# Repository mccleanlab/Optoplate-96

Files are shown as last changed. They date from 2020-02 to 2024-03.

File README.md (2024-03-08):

# OptoPlate-96
This repository contains the code  to calibrate and operate the [optoPlate-96](https://www.bugajlab.com/optoplate-96) and is intended to accompany the following paper:
E. O. S. Grødem, K. Sweeney, and M. N. McClean, “Automated calibration of optoPlate LEDs to reduce light dose variation in optogenetic experiments,” Biotechniques, vol. 69, no. 4, pp. 313–316, 2020.

To construct the optoPlate, see the original repository for the optoPlate-96 that can be found [here](https://github.com/BugajLab/optoPlate-96/) (as described in Bugaj and Lim, "High-throughput multicolor optogenetics in microwell plates" _Nature Protocols_ 14(7):2205-2228).

This repository was created to provide these features for the optoPlate-96:
- MATLAB interface for operation of the optoPlate-96.
- Functionality for calibration of the light intensities of the LEDs.
- Supports two levels of pulses to reduce the risk of phototoxicity.
- Visualisaztion of light patterns before an experiment.
- MultiColor LED support
- Support for turning on and off LED from a connected computer for microscope imagining

Machine learning scripts and data accompanying "Dynamic Multiplexed Control and Modeling of Optogenetic Systems Using the High-Throughput Optogenetic Platform, Lustro" (Harmer et al, BioRxiv 2023) can be found [here](https://github.com/zavalab/ML/tree/master/Optogenetics/)

Instructions and images for assembling the optoPlate with necessary adaptors can be found under "Mechanical".

## Installation:

- Install MATLAB
- Install Microsoft's Visual Studio Code and PlatformIO IDE by following these [instructions](https://platformio.org/install/ide?install=vscode)
- Install Platformio Shell Commands
  - In Windows Search, search for and then select: System (Control Panel)
  - Click the Advanced system settings link.
  - Click Environment Variables. In the section System Variables, find the PATH environment variable and select it. Click Edit. If the PATH environment variable does not exist, click New.
  - In the Edit enviroment variable window, create a new Path and paste `C:\Users\UserName\.platformio\penv\Scripts`. Make sure the new Path is on the top of the list. 
  - Click OK. Close all remaining windows by clicking OK.
You should now be able to flash the optoPlate-96 from your computer.

## Getting Started
If the optoPlate-96 has never been used before, it must be flashed with calibration values. Ideally the calibration procedure should be followed to calibrate the optoPlate to ensure consistent light intensities in the different wells. However, the optoPlate-96 will function with the default calibration values.
To flash the default calibration values, make sure the optoPlate is connected to the PC with an USB cable annd run the file calibration/FlashCalibration.m and select calibration/calibration_files/cal_round_0.mat. For instructions on how to calibrate the optoPlate see this article. 

To create an experiment, follow this procedure:
Create the following matrices:
- amplitudes [8 by 12 matrix of unsigned 8 bit integer] - light intensity of each LED, 255 - max light intensity and 0 - no light
- pulse_numbs [8 by 12 matrix of unsigned 16 bit integer] - number of pulses for each LED
- pusle_start_times [8 by 12 matrix of unsigned 16 bit integer] - time in seconds before sequence of pulses starts
- pulse_high_times [8 by 12 matrix of unsigned 16 bit integer] - time in seconds for high phase of pulse
- pulse_low_times [8 by 12 matrix of unsigned 16 bit integer] - time in seconds for low phase of pulse
- (optional) subpulse_high_times [8 by 12 matrix of unsigned 16 bit integer] - time in seconds for high phase of subpulse
- (optional) subpulse_low_times [8 by 12 matrix of unsigned 16 bit integer] - time in seconds for low phase of subpulse
Each cell in the matrices corresponds to a light well on the OptoPlate. For example, (1,1) is well A01 and (8,12) is well H12
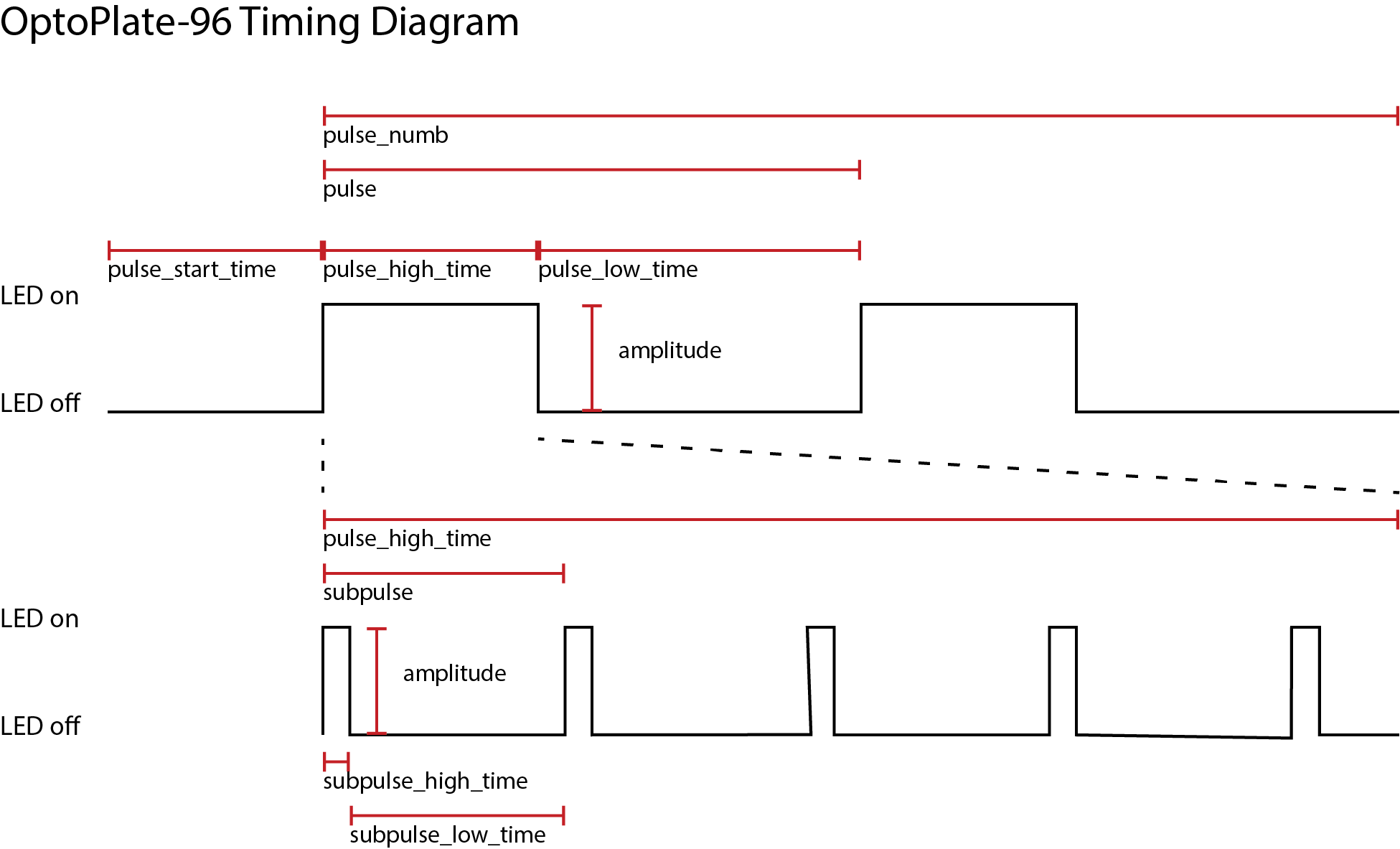
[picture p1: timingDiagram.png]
Timing Diagram

Create and save an experiment file by calling the function experiment/createExperiment.m
Make sure the OptoPlate is connected to the computer via an USB cable. Run the script experiment/FlashExperiment.m and select the experiment file.
The experiment will start immediately and will continue as long as the Arduino on the OptoPlate has power either through the USB cable or the 7V input. If power is cut to the Arduino, the experiment will reset. The experiment will also reset if the reset button on the Arduino is pressed.

## UART communication
Each well of the OptoPlate can be turned on and off by sending a UART message from the computer. This feature was added to support imagining with a microscope during an experiment. A detaljed description of how this works and a uart driver is provided in the folder OptoPlateDriver.

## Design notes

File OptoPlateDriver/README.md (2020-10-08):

# OptoPlate UART Driver 
This folder contains a driver written for use with the software NIS-elements AR. A custom driver can with ease be written for other purposes. '

## OptoPlate with NIS-elements AR
The diver can be imported into NIS micro. 
1. Visual Studio must be installed on the computer
2. To enable NIS to import the driver, copy the folder Optoplate-96/OptoPlateDiver/OptoPlate to the NIS installation folder most likely located in C:/Program Files/NIS-Elements. When this is done you should have the following file strucure: C:/Program Files/NIS-Elements/OptoPlate/OptoPlateDriver.dll
NIS Micros can now send commands to the OptoPlate. 

The following example of a micro will connect to Serial Port 14 and turn off all the LEDs in well 15 (B3). 
The OptoPlateConnectAuto() will search through the all connected serial ports and connect to one of them, this function can be used if the OptoPlate is the only serial port connected to the computer. In the case where there is more then one connected saerial port go to device manager in Windows to determine what port the optoPlate is connected to. It will be listed under "Ports (COM & LPT)" as "Arduino Micro Bootloader". Use the number after the COM in the function OptoPlateConnect(int) to connect to the optoPlate.  
Remember to always call OptoPlateConnect(int) or OptoPlateConnectAuto() before sending anything and always call OptoPlateDisconnect() before ending the program.
OptoPlateDiable(int) and OptoPlateEnable(int) takes an integer from 0 to 95 as input parameter. The index 15 correspond to the well B3 and index 16 to B4 and so on.  
```
import("OptoPlate\OptoPlateDriver.dll");
import int OptoPlateConnect(int portNumber);
import int OptoPlateConnectAuto();
import int OptoPlateDisconnect();
import int OptoPlateDisableLED(int LEDindex);
import int OptoPlateEnableLED(int LEDindex);

int main() {
   OptoPlateConnect(14);
   OptoPlateDisableLED(15);
   OptoPlateDisconnect();
   return 1;
}
                            
```
To change the index to be enable/diable while running a JOB module insert a Expression block. By opening the box you will get a list of all the variables used by the JOB module. The desired variable can then be used as parameter in the functions OptoPlateDiable(int) and OptoPlateEnable(int). A simple example is provided in Optoplate-96/OptoPlateDriver/NISexample    

## Help on implementation of custom driver
The OptoPlate accepts 1 byte messages over the Arduino Serial (UART) connection to the computer. The most significant bit is the enable/disable bit, the remaning 7 bits are the 0-indexed index of the well. For instance, by sending 0b0000 0010 over Serial, well A3 will turn off and 0b1000 1100 will enable enable well B1

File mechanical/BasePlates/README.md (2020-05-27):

The git repo for the original OptoPlate does not provide all the drawings for creating the aluminum plates in the assembly. 
These files can make the production of plates easier. 
They are taken from measurements and will therefore not be 100% precise.

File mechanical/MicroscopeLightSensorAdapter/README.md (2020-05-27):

Adaptor for mounting Thorlabs Standard Photodiode Power Sensors S12  to Nikon TiE inverted microscope

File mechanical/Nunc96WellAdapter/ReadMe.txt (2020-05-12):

Adapter for mounting a Nunc 265300 96 well plate to the OptoPlate. 
OptpPlateAdaperToNunc265300_Top is for mounting the 96 well plate upside down.

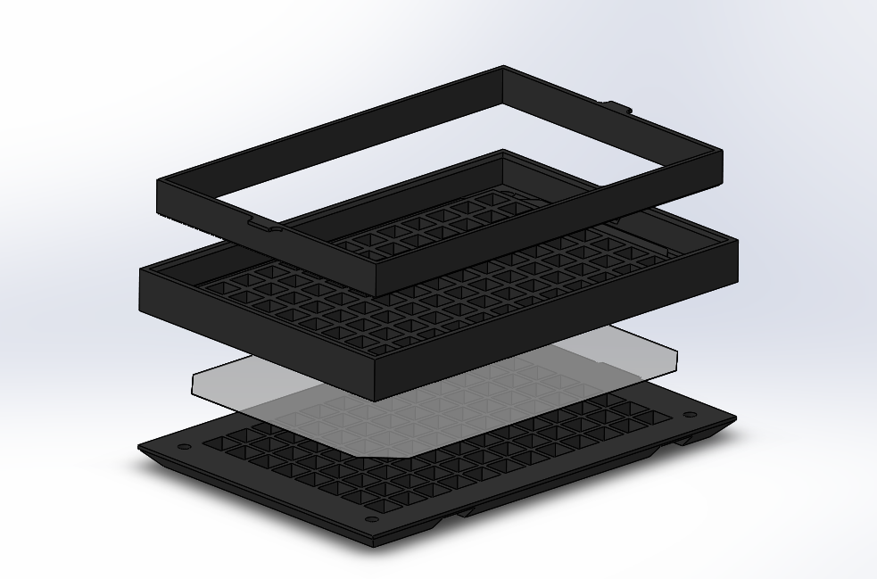
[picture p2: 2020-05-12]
mechanical/Nunc96WellAdapter/ExplodedViewRender.PNG

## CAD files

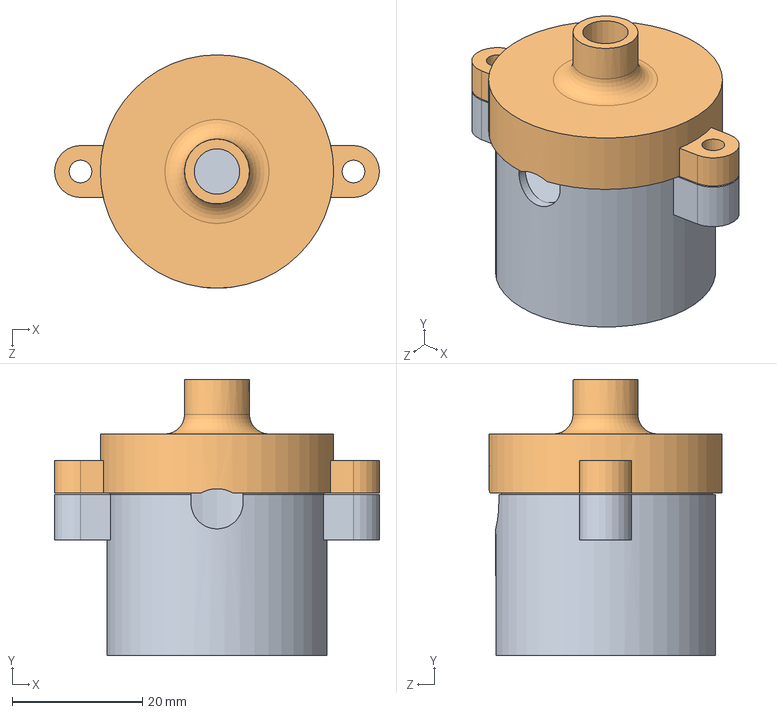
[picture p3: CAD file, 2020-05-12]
mechanical/MicroscopeLightSensorAdapter/AssemblyMicroscopeAdaptor.SLDASM
50.0 x 42.5 x 35.9 mm
MicroscopeAdapterLowerPart
MicroscopeAdapterUpperPart

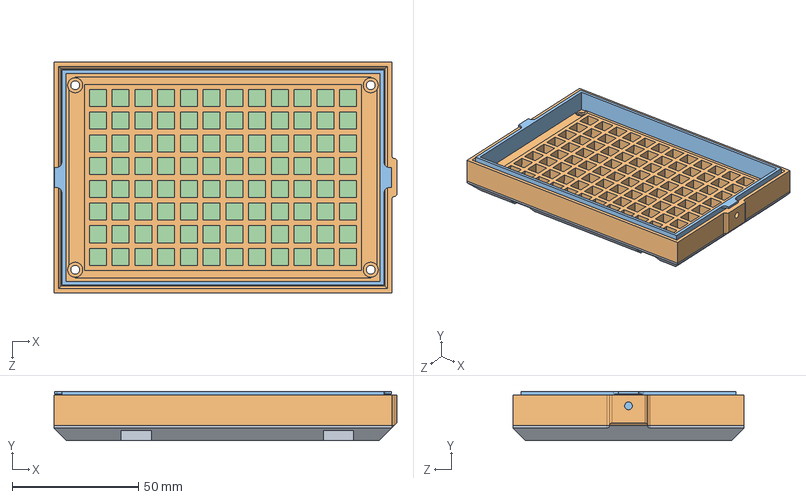
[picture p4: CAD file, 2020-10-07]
mechanical/Nunc96WellAdapter/OptoPlateAdapterToNunc265300_96_Assembly.SLDASM
135.8 x 19.5 x 91.5 mm
OptoPlateAdapterToNunc265300_96_BottomHalf
OptoPlateAdapterToNunc265300_96_Tophalf
Diffusion paper^OptoPlateAdapterToNunc265300_96_Assembly

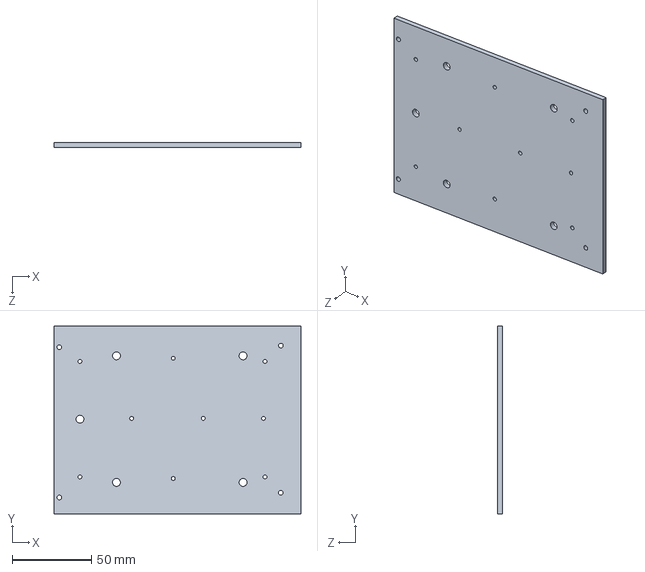
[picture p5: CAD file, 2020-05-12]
mechanical/BasePlates/Aluminum Plate.SLDPRT
156.1 x 118.5 x 3.17 mm

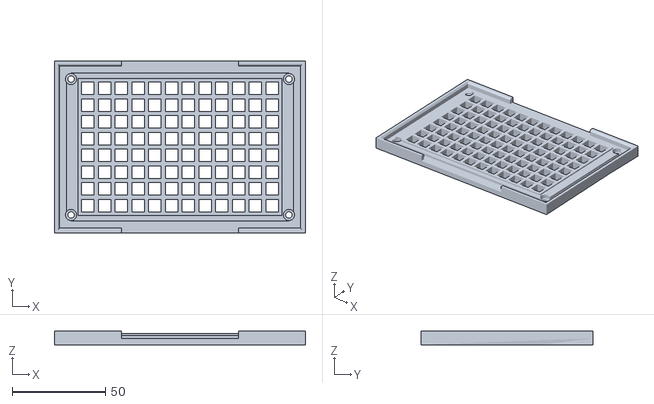
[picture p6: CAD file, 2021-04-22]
mechanical/Nunc96WellAdapter/3dprint/OptoPlateAdapterToNunc265300_96_Tophalf_TECAN.STL
134.8 x 92.5 x 7.29

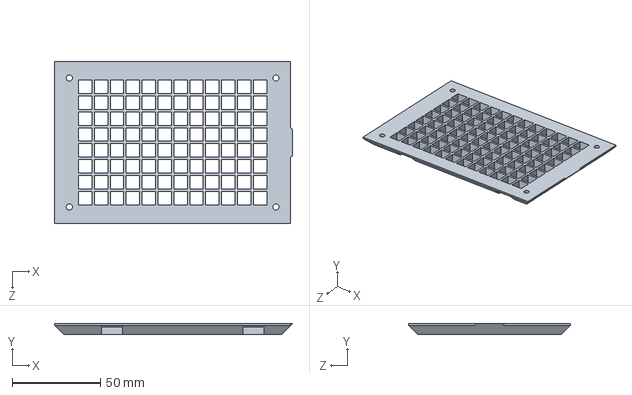
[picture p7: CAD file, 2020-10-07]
mechanical/Nunc96WellAdapter/OptoPlateAdapterToNunc265300_96_BottomHalf.sldprt
134.8 x 6.00 x 91.5 mm

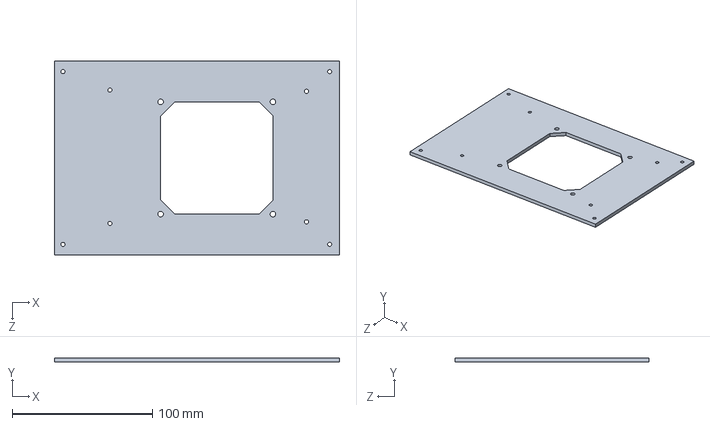
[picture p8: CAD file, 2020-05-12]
mechanical/BasePlates/Base Plate.SLDPRT
203.0 x 3.17 x 138.0 mm

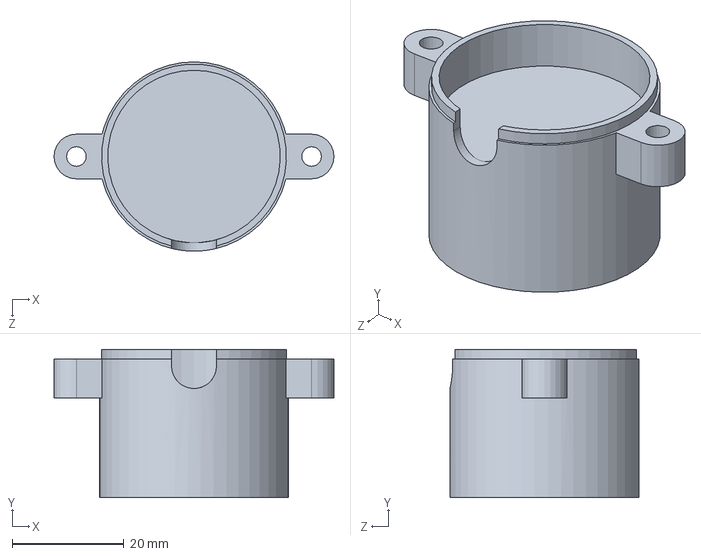
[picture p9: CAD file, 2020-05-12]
mechanical/MicroscopeLightSensorAdapter/MicroscopeAdaptorLowerPart.SLDPRT
50.0 x 26.5 x 33.8 mm

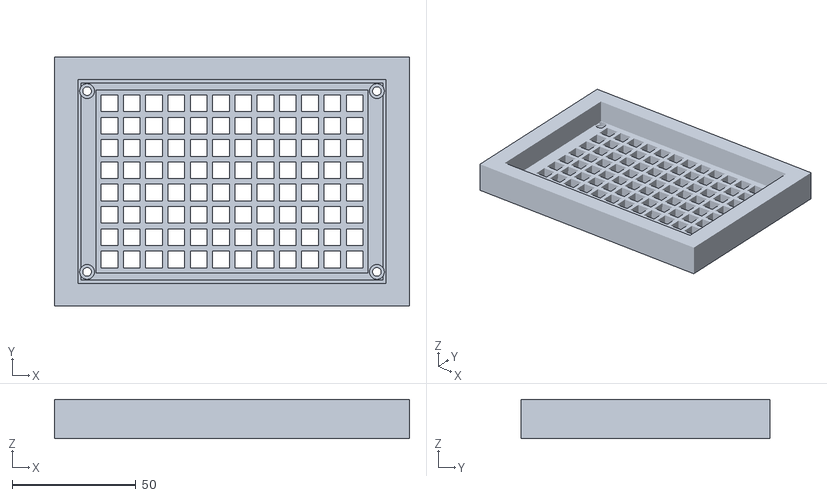
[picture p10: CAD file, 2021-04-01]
mechanical/Nunc96WellAdapter/3dprint/OptoPlateAdapterToNunc265300_96_Tophalf_Inverted.STL
143.3 x 100.5 x 15.9

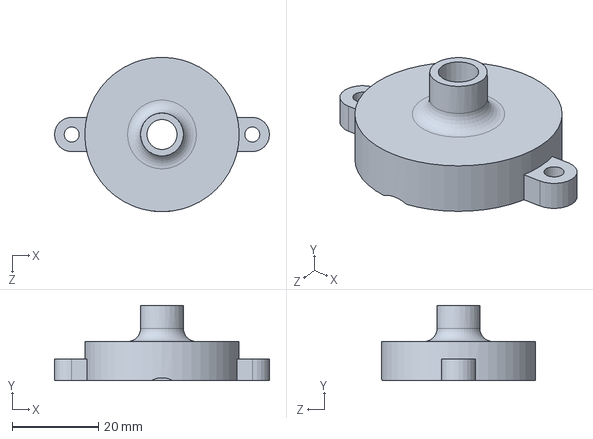
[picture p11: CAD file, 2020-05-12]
mechanical/MicroscopeLightSensorAdapter/MicroscopeAdaptorUpperPart.SLDPRT
50.0 x 17.5 x 35.9 mm

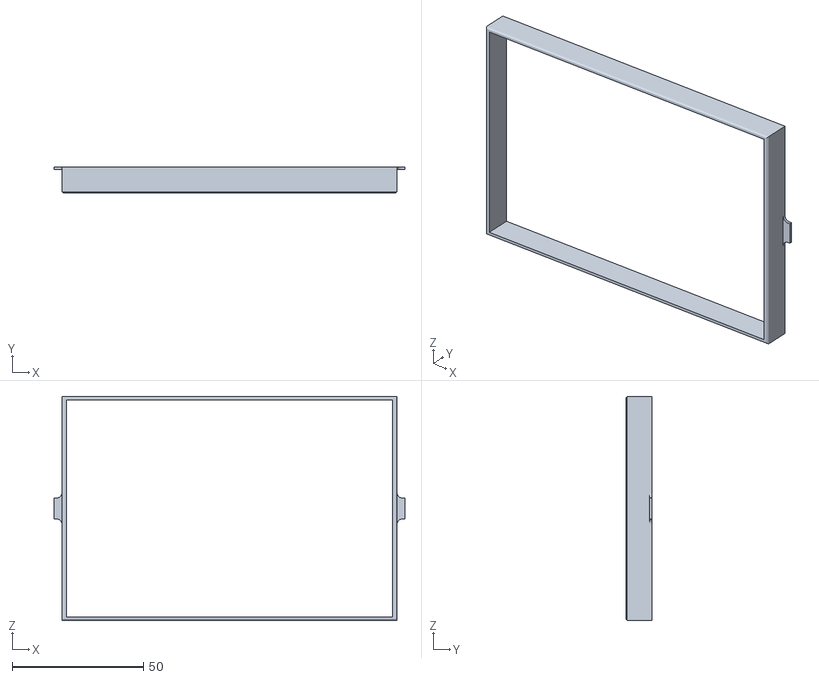
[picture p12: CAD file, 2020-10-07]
mechanical/Nunc96WellAdapter/3dprint/OptoPlateAdapterToNunc265300_96_InversionInsert_Default.STL
133.6 x 10.0 x 85.3

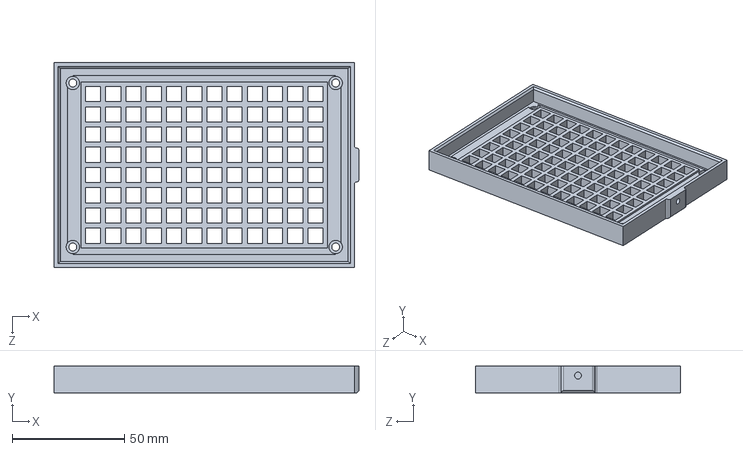
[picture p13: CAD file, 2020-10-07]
mechanical/Nunc96WellAdapter/OptoPlateAdapterToNunc265300_96_Tophalf.sldprt
135.8 x 12.0 x 91.5 mm

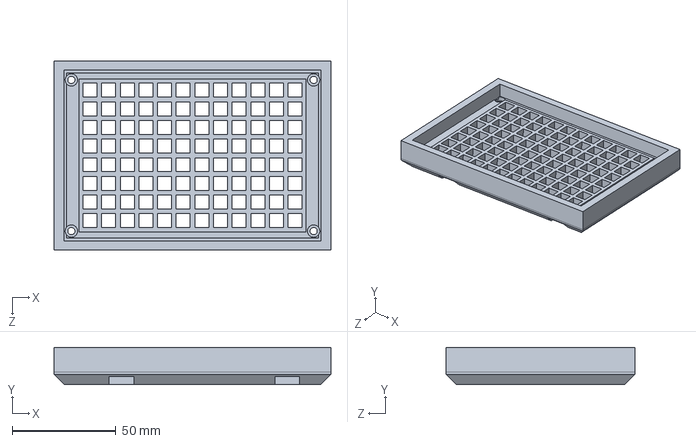
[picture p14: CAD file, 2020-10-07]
mechanical/Nunc96WellAdapter/OptoPlateAdapterToNunc265300_96.SLDPRT
133.8 x 18.0 x 91.5 mm

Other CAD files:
mechanical/Nunc96WellAdapter/3dprint/OptoPlateAdapterToNunc265300_96_BottomHalf_Default.STL
mechanical/Nunc96WellAdapter/3dprint/OptoPlateAdapterToNunc265300_96_Tophalf_Default.STL
mechanical/Nunc96WellAdapter/OptoPlateAdapterToNunc265300_96_InversionInsert.SLDPRT
mechanical/BasePlates/Aluminum Plate.SLDDRW
mechanical/BasePlates/Base Plate.SLDDRW

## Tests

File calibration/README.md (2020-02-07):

# optoPlate_calibration
 MATLAB script to calibrate optoPlate from images

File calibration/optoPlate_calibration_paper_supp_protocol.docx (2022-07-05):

Supplementary protocol

Configuring the optoPlate

We assemble the optoPlate as published [1], but with two changes to suit the needs of our lab and allow calibration. First, we adapt the optoPlate to accommodate 96 well optical-bottom plates (Nunc, #265300) via 3D printed adaptors. By default, these adaptors allow one to mount the 96 well plate on top of the optoPlate, though we also created a secondary adaptor to mount the optoPlate upside-down on top of the 96 well plate. The optoPlate can be equipped with these adaptors by following these steps (Figure S1):

1. Mount the optoPlateToNunc265300_BottomHalf adaptor to the optoPlate PCB
2. Place three diffuser sheets (Rosco, #3008) on top of the optoPlateToNunc265300_BottomHalf adaptor
3. Mount the optoPlateToNunc265300_TopHalf adaptor on top of the diffuser sheets. At this stage, a Nunc 96 well optical-bottom plate can be mounted on top of the optoPlate
4. Slot the optoPlateToNunc265300_Top adaptor into the optoPlateToNunc265300_TopHalf. The optoPlate can now be mounted upside-down on top of a Nunc 96 well optical-bottom plate.

Second, we developed new firmware for the optoPlate so the brightness of each LED is controlled by both a calibration value and an input value as follows:

LED intensity∝(input values)/255*(calibration values)/255

The input value is supplied by a user to control LED brightness over the course of an experiment. The calibration value must be set only once and accounts for brightness differences between LEDs, so that two LEDs set to the same input value will have the same brightness. The optoPlate firmware was built using PlatformIO and the onboard Arduino and it allows users to design LED light programs and flash them to the optoPlate using MATLAB.

The firmware and hardware used in this protocol are supplied in our supplementary materials. Updates will be made available on our GitHub page (github.com/mccleanlab/ OptoPlate-96). Installation of the firmware is described in detail in the included README file, as are instructions for creating light programs for experiments and flashing them to the optoPlate.

Calibrating the optoPlate with two LEDs

Our calibration method uses the programmable stage of a microscope to automatically move an optical power sensor over each optoPlate LED in a set order to acquire a timeseries of irradiance measurements from which the brightness of each LED can be determined and used to calculate calibration values. To ensure that each LED creates a distinct peak in the irradiance signal, we do not measure all the LEDs in one pass. Instead we measure all LEDs over the course of four passes in which we raster the optical power meter across the optoPlate such that every other LED encountered is inactive, leading to an irradiance signal in which measurements from inactive LEDs create clear troughs between measurements of bright LEDs. We do this by setting the optoPlate to deliver a checkerboard illumination pattern, such that no two illuminated wells are directly above, below, or beside each other in a given pass. We measure the remaining wells by setting the optoPlate to deliver the inverse checkerboard illumination pattern. Because each well of the optoPlate has two LEDs, we repeat this process twice, once for the left LED and once for the right LED. Once all 192 LEDs are measured, we analyze the irradiance measurements using a MATLAB script that determines the brightness of each LED and calculates a calibration value so that the brightest LEDs are dimmest to match the dimmest LED. We then flash the calibration values to the optoPlate and repeat the whole process until the coefficient of variation of the LED irradiance measurements falls below a set threshold (we use 1%).

In detail, this can be accomplished by following these steps (Figure S2):

1. First, mount a refocusing unit [2] to the active objective socket of a Nikon TiE inverted microscope. Then (as shown in Figure S3A) fasten the optical power sensor (Thorlabs S120VC) between the upper and lower optical power sensor adaptors (MicroscopeAdaptorLowerPart and MicroscopeAdaptorUpperPart, respectively) and mount the resulting assembly on the refocusing unit. Then connect the Thorlabs power sensor to a Thorlabs power meter (PM100D), which should be connected to a computer running Thorlabs Optical Power Monitor Version 1.1 software.
2. Mount a Nunc 96 well optical-bottom plate to the microscope stage (Figure S3B). Then mount the optoPlate upside-down on top of the 96 well plate via the optoPlateToNunc265300_Top adaptor. The optoPlate should be positioned so that well A1 of the optoPlate is positioned over well A12 of the 96 well plate. Plug in the optoPlate and connect it to a computer via the USB cable. To finish preparing the microscope for calibration, adjust its focus knob to raise the optical power sensor until it nearly touches the 96 well plate. Note the z-position of the stage and use it for all future measurements (we always use a z-position of 4000 μm). This approach allows consistent micron level precision when setting the distance between the optical power sensor and optoPlate.
3. Flash the initial set of calibration values to the optoPlate by running the MATLAB script ‘flash_calibration.m’ and selecting the file ‘cal_round_0’ at the prompt. This sets the initial calibration value of each LED to 255.
4. Making sure that the optical power meter is set to measure the appropriate wavelength for each set of LEDs, measure the brightness of the LEDs by using the programmable microscope stage to raster the optical power sensor across the 96 well plate:
  a. Flash the first checkerboard illumination pattern to the optoPlate by running ‘FlashExperiment.m’ and selecting ‘CHECKER01.mat’ when prompted. Then unplug the power cable for the right LEDs so that only the left LEDs of every other well are active. Start recording irradiance measurements with the power meter software, then have the microscope stage raster through the 96 well plate, pausing at each well for 3 s (Figure 1A). We did this via a NIS Elements JOBs module program. Save these measurements as ‘ROUND01_LED01_CHECKER01.csv’; they should resemble the signals depicted in Figure 1B.
  b. Unplug the power cable for the left LEDs and plug in the power cable for the right LEDs, then record LED irradiance measurements as described in step 4a. Save these measurements as ‘ROUND01_LED02_CHECKER01.csv’.
  c. Flash the second checkerboard illumination pattern to the optoPlate by running ‘flash_experiment.m’ and selecting ‘CHECKER02.mat’ when prompted. Record the LED irradiance measurements for both sets of LEDs as described above and save them as ‘ROUND01_LED01_CHECKER02.csv’ and ‘ROUND01_LED02_CHECKER02.csv’.
5. With all LEDs now measured, run the MATLAB script ‘optoPlate_calibration.m’ and select the saved ‘.csv’ files at the prompt. Note that this script uses the GRAMM toolbox for plotting, which can be found, along with installation instructions, at github.com/piermorel/gramm. The script will automatically identify each LED from the irradiance measurements and calculate calibration values, which are saved as ‘cal_round_1.mat’. It should be noted that this script assumes the wells are measured in a set order in which 1) the microscope rasters through a 96 well plate mounted on its programmable stage from A1-A12 to B12-B1 and so on and 2) the optoPlate is flipped when mounted upside-down on the 96 well plate so that these measurements actually correspond to optoPlate wells A12-A1 to B1-B12 etc. Flashing the optoPlate with CHECKER01.mat sets the checkerboard pattern in which the LEDs of optoPlate well A01 are active, while CHECKER02.mat sets the checkerboard pattern in which the LEDs of optoPlate well A01 are inactive. By default, the calibration script assumes an optoPlate configuration with two LEDs of the same color per well. If this is not the case, set the variable ‘calibrate_LEDs_independently’ to true and the script will treat each set of LEDs (LED01, LED02, etc.) as separate groups of different colored LEDs when calculating calibration values.
6. Flash the updated calibration values to the optoPlate. This concludes round one of calibration. The brightness of the LEDs should be much more uniform, though more rounds of calibration may be needed to further reduce brightness differences between LEDs.
7. Repeat steps 4 – 6 as needed until the coefficient of variation of the LED irradiance measurements falls below a set threshold (we chose 1%). Each of these repeats constitutes another round of calibration. When saving the ‘csv’ files, the round number should be included in the filename, for example, the left LED measurements for the first checkerboard illumination pattern of round two should be saved as ‘ROUND02_LED01_CHECKER01.csv’. Likewise, when loading the measurements into ‘optoPlate_calibration.m’ or flashing calibration values to the optoPlate, be sure to use the measurements or calibration values for the current round.

Calibrating an optoPlate with three LEDs

In the preceding protocol, we described the calibration of an optoPlate with two LEDs per well. However, an optoPlate can also be configured to have three different colored LEDs per well. In this case, the overall calibration process is similar, but involves six measurement passes—one per LED color for each checkerboard pattern. With three LEDs per well, one must switch between active LED sets by flashing checkerboard patterns for each color rather than reconnecting the power cables. As before, one must set ‘calibrate_LEDs_independently’ to true and set the optical power meter to measure the correct light wavelength for each set of LEDs.

Supplementary figure captions

Figure S1. Assembly of the optoPlate-to-Nunc265300 adaptors

Figure S2. A flow chart detailing the optoPlate calibration process

Figure S3. Overview of the components used for calibration. (A) An optical power meter is prepared for mounting on the microscope. (B) The optical power meter and optoPlate are mounted to a microscope.

1. Bugaj LJ, Lim WA. High-throughput multicolor optogenetics in microwell plates. Nat. Protoc. 14(7), 2205–2228 (2019).

2. Grünwald D, Shenoy SM, Burke S, Singer RH. Calibrating excitation light fluxes for quantitative light microscopy in cell biology. Nat. Protoc. 3(11), 1809–1814 (2008).

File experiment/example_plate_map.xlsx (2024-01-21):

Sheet: optoplate_config
LED1_amplitudes | 1 | 2 | 3 | 4 | 5 | 6 | 7 | 8 | 9 | 10 | 11 | 12 | LED2_amplitudes | 1 | 2 | 3 | 4 | 5 | 6 | 7 | 8 | 9 | 10 | 11 | 12 | LED3_amplitudes | 1 | 2 | 3 | 4 | 5 | 6 | 7 | 8 | 9 | 10 | 11 | 12
A | 0 | 128 | 0 | 128 | 0 | 0 | 0 | 0 | 0 | 0 | 0 | 0 | A |  |  |  |  |  |  |  |  |  |  |  |  | A
B | 20 | 128 | 20 | 128 | 0 | 0 | 0 | 0 | 0 | 0 | 0 | 0 | B |  |  |  |  |  |  |  |  |  |  |  |  | B
C | 45 | 128 | 45 | 128 | 0 | 0 | 0 | 0 | 0 | 0 | 0 | 0 | C |  |  |  |  |  |  |  |  |  |  |  |  | C
D | 85 | 128 | 85 | 128 | 0 | 0 | 0 | 0 | 0 | 0 | 0 | 0 | D |  |  |  |  |  |  |  |  |  |  |  |  | D
E | 128 | 128 | 128 | 128 | 0 | 0 | 0 | 0 | 0 | 0 | 0 | 0 | E |  |  |  |  |  |  |  |  |  |  |  |  | E
F | 128 | 128 | 128 | 128 | 0 | 0 | 0 | 0 | 0 | 0 | 0 | 0 | F |  |  |  |  |  |  |  |  |  |  |  |  | F
G | 128 | 128 | 128 | 128 | 0 | 0 | 0 | 0 | 0 | 0 | 0 | 0 | G |  |  |  |  |  |  |  |  |  |  |  |  | G
H | 128 | 128 | 128 | 0 | 0 | 0 | 0 | 0 | 0 | 0 | 0 | 0 | H |  |  |  |  |  |  |  |  |  |  |  |  | H
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

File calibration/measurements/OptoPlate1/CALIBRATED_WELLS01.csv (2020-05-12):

Optical Power Monitor
2.1.3076.429
Delimiter Used: | " | "
Start of Measurement | 3/11/2020 13:45:51
Sample Interval | 1 s
 | PM100D 15111301
Type | PM100D
Serialnumber | PM001960
Sensor | S120VC
SensorSerialnumber | 15111301
Wavelength / Responsivity | 488 nm
 |  |  | PM100D 15111301
Samples | Date (MM/dd/yyyy) | Time of day (hh:mm:ss) | Irradiance (W/cm²)
0 | 3/11/2020 | 13:45:51 | 1.4892E-07
1 | 3/11/2020 | 13:45:52 | 2.1814E-07
2 | 3/11/2020 | 13:45:53 | 2.0168E-07
3 | 3/11/2020 | 13:45:54 | 1.8654E-07
4 | 3/11/2020 | 13:45:55 | 2.392E-07
5 | 3/11/2020 | 13:45:56 | 1.8805E-07
6 | 3/11/2020 | 13:45:57 | 1.8052E-07
7 | 3/11/2020 | 13:45:58 | 1.5193E-07
8 | 3/11/2020 | 13:45:59 | 2.0911E-07
9 | 3/11/2020 | 13:46:00 | 1.8805E-07
10 | 3/11/2020 | 13:46:01 | 1.9707E-07
11 | 3/11/2020 | 13:46:02 | 5.8075E-07
12 | 3/11/2020 | 13:46:03 | 0.00017204
13 | 3/11/2020 | 13:46:04 | 0.00018895
14 | 3/11/2020 | 13:46:05 | 0.00018844
15 | 3/11/2020 | 13:46:06 | 9.2623E-05
16 | 3/11/2020 | 13:46:07 | 3.3248E-07
17 | 3/11/2020 | 13:46:08 | 3.1443E-07
18 | 3/11/2020 | 13:46:09 | 1.4444E-06
19 | 3/11/2020 | 13:46:10 | 0.00017526
20 | 3/11/2020 | 13:46:11 | 0.00018944
21 | 3/11/2020 | 13:46:12 | 0.00018967
22 | 3/11/2020 | 13:46:13 | 8.5935E-05
23 | 3/11/2020 | 13:46:14 | 3.6258E-07
24 | 3/11/2020 | 13:46:15 | 3.2948E-07
25 | 3/11/2020 | 13:46:16 | 3.3613E-06
26 | 3/11/2020 | 13:46:17 | 0.00018259
27 | 3/11/2020 | 13:46:18 | 0.00019082
28 | 3/11/2020 | 13:46:19 | 0.00018978
29 | 3/11/2020 | 13:46:20 | 0.00019081
30 | 3/11/2020 | 13:46:21 | 3.559E-05
31 | 3/11/2020 | 13:46:22 | 3.3851E-07
32 | 3/11/2020 | 13:46:23 | 3.0992E-07
33 | 3/11/2020 | 13:46:24 | 4.7949E-05
34 | 3/11/2020 | 13:46:25 | 0.00018731
35 | 3/11/2020 | 13:46:26 | 0.00018731
36 | 3/11/2020 | 13:46:27 | 0.00018752
37 | 3/11/2020 | 13:46:28 | 2.7843E-05
38 | 3/11/2020 | 13:46:29 | 3.385E-07
39 | 3/11/2020 | 13:46:30 | 2.9638E-07
40 | 3/11/2020 | 13:46:31 | 5.3616E-05
41 | 3/11/2020 | 13:46:32 | 0.00018876
42 | 3/11/2020 | 13:46:33 | 0.00018805
43 | 3/11/2020 | 13:46:34 | 0.00018868
44 | 3/11/2020 | 13:46:35 | 2.3159E-05
45 | 3/11/2020 | 13:46:36 | 3.2797E-07
46 | 3/11/2020 | 13:46:37 | 3.4452E-07
47 | 3/11/2020 | 13:46:38 | 5.9923E-05
48 | 3/11/2020 | 13:46:39 | 0.00019009
49 | 3/11/2020 | 13:46:40 | 0.00019072
50 | 3/11/2020 | 13:46:41 | 0.00018964
51 | 3/11/2020 | 13:46:42 | 2.5072E-05
52 | 3/11/2020 | 13:46:43 | 2.8885E-07
53 | 3/11/2020 | 13:46:44 | 3.0089E-07
54 | 3/11/2020 | 13:46:45 | 5.3238E-05
55 | 3/11/2020 | 13:46:46 | 0.00018887
56 | 3/11/2020 | 13:46:47 | 0.00018843
57 | 3/11/2020 | 13:46:48 | 0.0001883
58 | 3/11/2020 | 13:46:49 | 2.3934E-05
59 | 3/11/2020 | 13:46:50 | 4.3029E-07
60 | 3/11/2020 | 13:46:51 | 4.2126E-07
61 | 3/11/2020 | 13:46:52 | 5.6047E-05
62 | 3/11/2020 | 13:46:53 | 0.00018837
63 | 3/11/2020 | 13:46:54 | 0.0001875
64 | 3/11/2020 | 13:46:55 | 0.00018726
65 | 3/11/2020 | 13:46:56 | 2.0118E-05
66 | 3/11/2020 | 13:46:57 | 4.9047E-07
67 | 3/11/2020 | 13:46:58 | 4.7994E-07
68 | 3/11/2020 | 13:46:59 | 5.966E-05
69 | 3/11/2020 | 13:47:00 | 0.00019029
70 | 3/11/2020 | 13:47:01 | 0.00019017
71 | 3/11/2020 | 13:47:02 | 0.00018925
72 | 3/11/2020 | 13:47:03 | 1.7208E-05
73 | 3/11/2020 | 13:47:04 | 4.4382E-07
74 | 3/11/2020 | 13:47:05 | 4.1524E-07
75 | 3/11/2020 | 13:47:06 | 6.2761E-05
76 | 3/11/2020 | 13:47:07 | 0.00018796
77 | 3/11/2020 | 13:47:08 | 0.00018821
78 | 3/11/2020 | 13:47:09 | 0.00018833
79 | 3/11/2020 | 13:47:10 | 1.7293E-05
80 | 3/11/2020 | 13:47:11 | 4.5135E-07
81 | 3/11/2020 | 13:47:12 | 4.5586E-07
82 | 3/11/2020 | 13:47:13 | 6.5287E-05
83 | 3/11/2020 | 13:47:14 | 0.00018891
84 | 3/11/2020 | 13:47:15 | 0.0001879
85 | 3/11/2020 | 13:47:16 | 0.00018749
86 | 3/11/2020 | 13:47:17 | 1.3704E-05
87 | 3/11/2020 | 13:47:18 | 4.0471E-07
88 | 3/11/2020 | 13:47:19 | 3.9417E-07
89 | 3/11/2020 | 13:47:20 | 6.7406E-05
90 | 3/11/2020 | 13:47:21 | 0.00018756
91 | 3/11/2020 | 13:47:22 | 0.00018933
92 | 3/11/2020 | 13:47:23 | 0.0001866
93 | 3/11/2020 | 13:47:24 | 1.2404E-05
94 | 3/11/2020 | 13:47:25 | 3.365E-07
95 | 3/11/2020 | 13:47:26 | 3.6709E-07
96 | 3/11/2020 | 13:47:27 | 3.5204E-07
97 | 3/11/2020 | 13:47:28 | 0.00012836
98 | 3/11/2020 | 13:47:29 | 0.00018951
99 | 3/11/2020 | 13:47:30 | 0.00018942
100 | 3/11/2020 | 13:47:31 | 0.00013738
101 | 3/11/2020 | 13:47:32 | 4.7091E-07
102 | 3/11/2020 | 13:47:33 | 4.5436E-07
103 | 3/11/2020 | 13:47:34 | 4.1524E-07
104 | 3/11/2020 | 13:47:35 | 0.00012958
105 | 3/11/2020 | 13:47:36 | 0.0001887
106 | 3/11/2020 | 13:47:37 | 0.00018876
107 | 3/11/2020 | 13:47:38 | 0.00013406
108 | 3/11/2020 | 13:47:39 | 5.2357E-07
109 | 3/11/2020 | 13:47:40 | 4.1674E-07
110 | 3/11/2020 | 13:47:41 | 4.679E-07
111 | 3/11/2020 | 13:47:42 | 0.00013328
112 | 3/11/2020 | 13:47:43 | 0.00018759
113 | 3/11/2020 | 13:47:44 | 0.00018736
114 | 3/11/2020 | 13:47:45 | 0.00013211
115 | 3/11/2020 | 13:47:46 | 5.1605E-07
116 | 3/11/2020 | 13:47:47 | 4.4081E-07
117 | 3/11/2020 | 13:47:48 | 4.6941E-07
118 | 3/11/2020 | 13:47:49 | 0.00013591
119 | 3/11/2020 | 13:47:50 | 0.00018752
120 | 3/11/2020 | 13:47:51 | 0.00018766
121 | 3/11/2020 | 13:47:52 | 0.00012946
122 | 3/11/2020 | 13:47:53 | 4.5135E-07
123 | 3/11/2020 | 13:47:54 | 5.0401E-07
124 | 3/11/2020 | 13:47:55 | 4.5587E-07
125 | 3/11/2020 | 13:47:56 | 0.00013936
126 | 3/11/2020 | 13:47:57 | 0.00018807
127 | 3/11/2020 | 13:47:58 | 0.00018802
128 | 3/11/2020 | 13:47:59 | 0.00012273
129 | 3/11/2020 | 13:48:00 | 4.4533E-07
130 | 3/11/2020 | 13:48:01 | 4.047E-07
131 | 3/11/2020 | 13:48:02 | 4.6038E-07
132 | 3/11/2020 | 13:48:03 | 0.00014478
133 | 3/11/2020 | 13:48:04 | 0.00018847
134 | 3/11/2020 | 13:48:05 | 0.00018779
135 | 3/11/2020 | 13:48:06 | 0.00012703
136 | 3/11/2020 | 13:48:07 | 3.2045E-07
137 | 3/11/2020 | 13:48:08 | 2.9186E-07
138 | 3/11/2020 | 13:48:09 | 2.7381E-07
139 | 3/11/2020 | 13:48:10 | 0.00013569
140 | 3/11/2020 | 13:48:11 | 0.00018765
141 | 3/11/2020 | 13:48:12 | 0.00018697
142 | 3/11/2020 | 13:48:13 | 0.00012682
143 | 3/11/2020 | 13:48:14 | 4.5135E-07
144 | 3/11/2020 | 13:48:15 | 4.7091E-07
145 | 3/11/2020 | 13:48:16 | 4.3781E-07
146 | 3/11/2020 | 13:48:17 | 0.00014017
147 | 3/11/2020 | 13:48:18 | 0.00018579
148 | 3/11/2020 | 13:48:19 | 0.0001864
149 | 3/11/2020 | 13:48:20 | 0.0001247
150 | 3/11/2020 | 13:48:21 | 4.9799E-07
151 | 3/11/2020 | 13:48:22 | 4.4984E-07
152 | 3/11/2020 | 13:48:23 | 4.5285E-07
153 | 3/11/2020 | 13:48:24 | 0.00013965
154 | 3/11/2020 | 13:48:25 | 0.00018666
155 | 3/11/2020 | 13:48:26 | 0.00018718
156 | 3/11/2020 | 13:48:27 | 0.00012303
157 | 3/11/2020 | 13:48:28 | 4.8897E-07
158 | 3/11/2020 | 13:48:29 | 4.363E-07
159 | 3/11/2020 | 13:48:30 | 4.4984E-07
160 | 3/11/2020 | 13:48:31 | 0.0001445
161 | 3/11/2020 | 13:48:32 | 0.00018847
162 | 3/11/2020 | 13:48:33 | 0.00018728
163 | 3/11/2020 | 13:48:34 | 0.00018719
164 | 3/11/2020 | 13:48:35 | 6.9849E-05
165 | 3/11/2020 | 13:48:36 | 4.6188E-07
166 | 3/11/2020 | 13:48:37 | 4.3329E-07
167 | 3/11/2020 | 13:48:38 | 1.1388E-05
168 | 3/11/2020 | 13:48:39 | 0.00018791
169 | 3/11/2020 | 13:48:40 | 0.00018764
170 | 3/11/2020 | 13:48:41 | 0.00018962
171 | 3/11/2020 | 13:48:42 | 6.9074E-05
172 | 3/11/2020 | 13:48:43 | 4.6941E-07
173 | 3/11/2020 | 13:48:44 | 4.378E-07
174 | 3/11/2020 | 13:48:45 | 1.3236E-05
175 | 3/11/2020 | 13:48:46 | 0.00018874
176 | 3/11/2020 | 13:48:47 | 0.00018898
177 | 3/11/2020 | 13:48:48 | 0.0001898
178 | 3/11/2020 | 13:48:49 | 6.3995E-05
179 | 3/11/2020 | 13:48:50 | 3.4903E-07
180 | 3/11/2020 | 13:48:51 | 2.8133E-07
181 | 3/11/2020 | 13:48:52 | 2.3001E-05
182 | 3/11/2020 | 13:48:53 | 0.00018928
183 | 3/11/2020 | 13:48:54 | 0.00018957
184 | 3/11/2020 | 13:48:55 | 0.00019044
185 | 3/11/2020 | 13:48:56 | 5.4797E-05
186 | 3/11/2020 | 13:48:57 | 4.2878E-07
187 | 3/11/2020 | 13:48:58 | 4.5586E-07
188 | 3/11/2020 | 13:48:59 | 2.2631E-05
189 | 3/11/2020 | 13:49:00 | 0.00018758
190 | 3/11/2020 | 13:49:01 | 0.00018717
191 | 3/11/2020 | 13:49:02 | 0.00018835
192 | 3/11/2020 | 13:49:03 | 5.5995E-05
193 | 3/11/2020 | 13:49:04 | 4.9649E-07
194 | 3/11/2020 | 13:49:05 | 4.6188E-07
195 | 3/11/2020 | 13:49:06 | 2.2676E-05
196 | 3/11/2020 | 13:49:07 | 0.00018856
197 | 3/11/2020 | 13:49:08 | 0.00018779
198 | 3/11/2020 | 13:49:09 | 0.00018901
199 | 3/11/2020 | 13:49:10 | 5.57E-05
200 | 3/11/2020 | 13:49:11 | 4.9649E-07
201 | 3/11/2020 | 13:49:12 | 5.0251E-07
202 | 3/11/2020 | 13:49:13 | 2.5658E-05
203 | 3/11/2020 | 13:49:14 | 0.00018671
204 | 3/11/2020 | 13:49:15 | 0.00018759
205 | 3/11/2020 | 13:49:16 | 0.0001862
206 | 3/11/2020 | 13:49:17 | 5.2502E-05
207 | 3/11/2020 | 13:49:18 | 4.9348E-07
208 | 3/11/2020 | 13:49:19 | 4.348E-07
209 | 3/11/2020 | 13:49:20 | 2.6501E-05
210 | 3/11/2020 | 13:49:21 | 0.0001865
211 | 3/11/2020 | 13:49:22 | 0.00018691
212 | 3/11/2020 | 13:49:23 | 0.00018749
213 | 3/11/2020 | 13:49:24 | 5.0734E-05
214 | 3/11/2020 | 13:49:25 | 3.9869E-07
215 | 3/11/2020 | 13:49:26 | 3.8214E-07
216 | 3/11/2020 | 13:49:27 | 2.795E-05
217 | 3/11/2020 | 13:49:28 | 0.00018809
218 | 3/11/2020 | 13:49:29 | 0.00018803
219 | 3/11/2020 | 13:49:30 | 0.000188
220 | 3/11/2020 | 13:49:31 | 5.6905E-05
221 | 3/11/2020 | 13:49:32 | 2.8133E-07
222 | 3/11/2020 | 13:49:33 | 3.0691E-07
223 | 3/11/2020 | 13:49:34 | 2.0934E-05
224 | 3/11/2020 | 13:49:35 | 0.00018661
225 | 3/11/2020 | 13:49:36 | 0.00018725
226 | 3/11/2020 | 13:49:37 | 0.00018675
227 | 3/11/2020 | 13:49:38 | 5.5951E-05
228 | 3/11/2020 | 13:49:39 | 4.6038E-07
229 | 3/11/2020 | 13:49:40 | 4.7994E-07
230 | 3/11/2020 | 13:49:41 | 2.3869E-05
231 | 3/11/2020 | 13:49:42 | 0.00018736
232 | 3/11/2020 | 13:49:43 | 0.00018781
233 | 3/11/2020 | 13:49:44 | 0.00018732
234 | 3/11/2020 | 13:49:45 | 0.00018384
235 | 3/11/2020 | 13:49:46 | 5.9929E-06
236 | 3/11/2020 | 13:49:47 | 4.679E-07
237 | 3/11/2020 | 13:49:48 | 4.1373E-07
238 | 3/11/2020 | 13:49:49 | 7.8054E-05
239 | 3/11/2020 | 13:49:50 | 0.0001881
240 | 3/11/2020 | 13:49:51 | 0.00018845
241 | 3/11/2020 | 13:49:52 | 0.00018283
242 | 3/11/2020 | 13:49:53 | 4.6763E-06
243 | 3/11/2020 | 13:49:54 | 4.7241E-07
244 | 3/11/2020 | 13:49:55 | 4.7843E-07
245 | 3/11/2020 | 13:49:56 | 7.9555E-05
246 | 3/11/2020 | 13:49:57 | 0.00018704
247 | 3/11/2020 | 13:49:58 | 0.00018805
248 | 3/11/2020 | 13:49:59 | 0.00018266
249 | 3/11/2020 | 13:50:00 | 5.1608E-06
250 | 3/11/2020 | 13:50:01 | 4.8295E-07
251 | 3/11/2020 | 13:50:02 | 4.3781E-07
252 | 3/11/2020 | 13:50:03 | 8.1584E-05
253 | 3/11/2020 | 13:50:04 | 0.0001876
254 | 3/11/2020 | 13:50:05 | 0.00018803
255 | 3/11/2020 | 13:50:06 | 0.00018042
256 | 3/11/2020 | 13:50:07 | 4.082E-06
257 | 3/11/2020 | 13:50:08 | 4.2727E-07
258 | 3/11/2020 | 13:50:09 | 3.9719E-07
259 | 3/11/2020 | 13:50:10 | 8.2523E-05
260 | 3/11/2020 | 13:50:11 | 0.00018856
261 | 3/11/2020 | 13:50:12 | 0.00018798
262 | 3/11/2020 | 13:50:13 | 0.00017881
263 | 3/11/2020 | 13:50:14 | 3.0905E-06
264 | 3/11/2020 | 13:50:15 | 3.1894E-07
265 | 3/11/2020 | 13:50:16 | 3.1293E-07
266 | 3/11/2020 | 13:50:17 | 9.3127E-05
267 | 3/11/2020 | 13:50:18 | 0.00018834
268 | 3/11/2020 | 13:50:19 | 0.00018876
269 | 3/11/2020 | 13:50:20 | 0.00017357
270 | 3/11/2020 | 13:50:21 | 1.0051E-06
271 | 3/11/2020 | 13:50:22 | 4.4232E-07
272 | 3/11/2020 | 13:50:23 | 4.4232E-07
273 | 3/11/2020 | 13:50:24 | 9.6479E-05
274 | 3/11/2020 | 13:50:25 | 0.00018815
275 | 3/11/2020 | 13:50:26 | 0.00018835
276 | 3/11/2020 | 13:50:27 | 0.00017052
277 | 3/11/2020 | 13:50:28 | 7.8688E-07
278 | 3/11/2020 | 13:50:29 | 4.333E-07
279 | 3/11/2020 | 13:50:30 | 4.3029E-07
280 | 3/11/2020 | 13:50:31 | 9.7841E-05
281 | 3/11/2020 | 13:50:32 | 0.00018885
282 | 3/11/2020 | 13:50:33 | 0.00018821
283 | 3/11/2020 | 13:50:34 | 0.0001679
284 | 3/11/2020 | 13:50:35 | 5.7924E-07
285 | 3/11/2020 | 13:50:36 | 4.2277E-07
286 | 3/11/2020 | 13:50:37 | 4.348E-07
287 | 3/11/2020 | 13:50:38 | 0.00010308
288 | 3/11/2020 | 13:50:39 | 0.00018814
289 | 3/11/2020 | 13:50:40 | 0.00018701
290 | 3/11/2020 | 13:50:41 | 0.00016323
291 | 3/11/2020 | 13:50:42 | 5.4464E-07
292 | 3/11/2020 | 13:50:43 | 4.2426E-07
293 | 3/11/2020 | 13:50:44 | 4.4232E-07
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

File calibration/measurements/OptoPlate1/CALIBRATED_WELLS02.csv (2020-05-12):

Optical Power Monitor
2.1.3076.429
Delimiter Used: | " | "
Start of Measurement | 3/11/2020 13:53:24
Sample Interval | 1 s
 | PM100D 15111301
Type | PM100D
Serialnumber | PM001960
Sensor | S120VC
SensorSerialnumber | 15111301
Wavelength / Responsivity | 488 nm
 |  |  | PM100D 15111301
Samples | Date (MM/dd/yyyy) | Time of day (hh:mm:ss) | Irradiance (W/cm²)
0 | 3/11/2020 | 13:53:24 | 5.4613E-07
1 | 3/11/2020 | 13:53:26 | 2.9938E-07
2 | 3/11/2020 | 13:53:27 | 3.1593E-07
3 | 3/11/2020 | 13:53:28 | 3.1443E-07
4 | 3/11/2020 | 13:53:29 | 3.039E-07
5 | 3/11/2020 | 13:53:30 | 2.8735E-07
6 | 3/11/2020 | 13:53:31 | 3.054E-07
7 | 3/11/2020 | 13:53:32 | 0.00013712
8 | 3/11/2020 | 13:53:33 | 0.00019022
9 | 3/11/2020 | 13:53:34 | 0.00019034
10 | 3/11/2020 | 13:53:35 | 0.00012233
11 | 3/11/2020 | 13:53:36 | 3.5204E-07
12 | 3/11/2020 | 13:53:37 | 2.8735E-07
13 | 3/11/2020 | 13:53:38 | 2.8735E-07
14 | 3/11/2020 | 13:53:39 | 0.00014848
15 | 3/11/2020 | 13:53:40 | 0.00019044
16 | 3/11/2020 | 13:53:41 | 0.00018943
17 | 3/11/2020 | 13:53:42 | 0.00011448
18 | 3/11/2020 | 13:53:43 | 3.37E-07
19 | 3/11/2020 | 13:53:44 | 2.8284E-07
20 | 3/11/2020 | 13:53:45 | 2.9337E-07
21 | 3/11/2020 | 13:53:46 | 0.00015699
22 | 3/11/2020 | 13:53:47 | 0.0001893
23 | 3/11/2020 | 13:53:48 | 0.00018901
24 | 3/11/2020 | 13:53:49 | 0.00010931
25 | 3/11/2020 | 13:53:50 | 3.6709E-07
26 | 3/11/2020 | 13:53:51 | 3.9267E-07
27 | 3/11/2020 | 13:53:52 | 4.0621E-07
28 | 3/11/2020 | 13:53:53 | 0.00016219
29 | 3/11/2020 | 13:53:54 | 0.0001891
30 | 3/11/2020 | 13:53:55 | 0.00018901
31 | 3/11/2020 | 13:53:56 | 0.00010204
32 | 3/11/2020 | 13:53:57 | 3.8364E-07
33 | 3/11/2020 | 13:53:58 | 3.2797E-07
34 | 3/11/2020 | 13:53:59 | 4.4534E-07
35 | 3/11/2020 | 13:54:00 | 0.00016646
36 | 3/11/2020 | 13:54:01 | 0.00018799
37 | 3/11/2020 | 13:54:02 | 0.000188
38 | 3/11/2020 | 13:54:03 | 9.6457E-05
39 | 3/11/2020 | 13:54:04 | 3.0089E-07
40 | 3/11/2020 | 13:54:05 | 3.1894E-07
41 | 3/11/2020 | 13:54:06 | 1.2729E-06
42 | 3/11/2020 | 13:54:07 | 0.0001755
43 | 3/11/2020 | 13:54:08 | 0.00018832
44 | 3/11/2020 | 13:54:09 | 0.0001881
45 | 3/11/2020 | 13:54:10 | 8.5043E-05
46 | 3/11/2020 | 13:54:11 | 2.1362E-07
47 | 3/11/2020 | 13:54:12 | 1.8654E-07
48 | 3/11/2020 | 13:54:13 | 1.8943E-06
49 | 3/11/2020 | 13:54:14 | 0.00017735
50 | 3/11/2020 | 13:54:15 | 0.00018818
51 | 3/11/2020 | 13:54:16 | 0.00018825
52 | 3/11/2020 | 13:54:17 | 8.403E-05
53 | 3/11/2020 | 13:54:18 | 3.365E-07
54 | 3/11/2020 | 13:54:19 | 4.1825E-07
55 | 3/11/2020 | 13:54:20 | 4.0772E-07
56 | 3/11/2020 | 13:54:21 | 5.2513E-05
57 | 3/11/2020 | 13:54:22 | 0.0001877
58 | 3/11/2020 | 13:54:23 | 0.00018793
59 | 3/11/2020 | 13:54:24 | 0.00018709
60 | 3/11/2020 | 13:54:25 | 2.0743E-05
61 | 3/11/2020 | 13:54:26 | 4.679E-07
62 | 3/11/2020 | 13:54:27 | 4.3781E-07
63 | 3/11/2020 | 13:54:28 | 5.9676E-05
64 | 3/11/2020 | 13:54:29 | 0.00018876
65 | 3/11/2020 | 13:54:30 | 0.00018854
66 | 3/11/2020 | 13:54:31 | 0.00018849
67 | 3/11/2020 | 13:54:32 | 1.6468E-05
68 | 3/11/2020 | 13:54:33 | 4.6339E-07
69 | 3/11/2020 | 13:54:34 | 4.1975E-07
70 | 3/11/2020 | 13:54:35 | 6.5636E-05
71 | 3/11/2020 | 13:54:36 | 0.00018919
72 | 3/11/2020 | 13:54:37 | 0.00018926
73 | 3/11/2020 | 13:54:38 | 0.00018759
74 | 3/11/2020 | 13:54:39 | 1.2252E-05
75 | 3/11/2020 | 13:54:40 | 4.1073E-07
76 | 3/11/2020 | 13:54:41 | 4.0772E-07
77 | 3/11/2020 | 13:54:42 | 7.0015E-05
78 | 3/11/2020 | 13:54:43 | 0.00018845
79 | 3/11/2020 | 13:54:44 | 0.00018922
80 | 3/11/2020 | 13:54:45 | 0.00018707
81 | 3/11/2020 | 13:54:46 | 9.127E-06
82 | 3/11/2020 | 13:54:47 | 4.6339E-07
83 | 3/11/2020 | 13:54:48 | 3.9719E-07
84 | 3/11/2020 | 13:54:49 | 7.5553E-05
85 | 3/11/2020 | 13:54:50 | 0.00019053
86 | 3/11/2020 | 13:54:51 | 0.00018992
87 | 3/11/2020 | 13:54:52 | 0.00018401
88 | 3/11/2020 | 13:54:53 | 5.1428E-06
89 | 3/11/2020 | 13:54:54 | 3.4151E-07
90 | 3/11/2020 | 13:54:55 | 3.2797E-07
91 | 3/11/2020 | 13:54:56 | 8.2423E-05
92 | 3/11/2020 | 13:54:57 | 0.00018876
93 | 3/11/2020 | 13:54:58 | 0.0001892
94 | 3/11/2020 | 13:54:59 | 0.00017083
95 | 3/11/2020 | 13:55:00 | 8.4556E-07
96 | 3/11/2020 | 13:55:01 | 4.2728E-07
97 | 3/11/2020 | 13:55:02 | 3.7763E-07
98 | 3/11/2020 | 13:55:03 | 9.9686E-05
99 | 3/11/2020 | 13:55:04 | 0.00018827
100 | 3/11/2020 | 13:55:05 | 0.00018818
101 | 3/11/2020 | 13:55:06 | 0.00016221
102 | 3/11/2020 | 13:55:07 | 5.4464E-07
103 | 3/11/2020 | 13:55:08 | 5.02E-07
104 | 3/11/2020 | 13:55:09 | 5.1454E-07
105 | 3/11/2020 | 13:55:10 | 5.2808E-07
106 | 3/11/2020 | 13:55:11 | 0.00016197
107 | 3/11/2020 | 13:55:12 | 0.00018922
108 | 3/11/2020 | 13:55:13 | 0.00018896
109 | 3/11/2020 | 13:55:14 | 0.00010494
110 | 3/11/2020 | 13:55:15 | 4.7091E-07
111 | 3/11/2020 | 13:55:16 | 4.4383E-07
112 | 3/11/2020 | 13:55:17 | 8.3353E-07
113 | 3/11/2020 | 13:55:18 | 0.00016869
114 | 3/11/2020 | 13:55:19 | 0.00018733
115 | 3/11/2020 | 13:55:20 | 0.00018716
116 | 3/11/2020 | 13:55:21 | 9.4632E-05
117 | 3/11/2020 | 13:55:22 | 4.5586E-07
118 | 3/11/2020 | 13:55:23 | 5.1906E-07
119 | 3/11/2020 | 13:55:24 | 1.1826E-06
120 | 3/11/2020 | 13:55:25 | 0.00017237
121 | 3/11/2020 | 13:55:26 | 0.00018902
122 | 3/11/2020 | 13:55:27 | 0.00018917
123 | 3/11/2020 | 13:55:28 | 9.418E-05
124 | 3/11/2020 | 13:55:29 | 5.2959E-07
125 | 3/11/2020 | 13:55:30 | 4.9498E-07
126 | 3/11/2020 | 13:55:31 | 2.0192E-06
127 | 3/11/2020 | 13:55:32 | 0.00017484
128 | 3/11/2020 | 13:55:33 | 0.00018768
129 | 3/11/2020 | 13:55:34 | 0.00018752
130 | 3/11/2020 | 13:55:35 | 8.8726E-05
131 | 3/11/2020 | 13:55:36 | 3.6559E-07
132 | 3/11/2020 | 13:55:37 | 3.2496E-07
133 | 3/11/2020 | 13:55:38 | 5.3711E-07
134 | 3/11/2020 | 13:55:39 | 0.00016929
135 | 3/11/2020 | 13:55:40 | 0.00018871
136 | 3/11/2020 | 13:55:41 | 0.00018892
137 | 3/11/2020 | 13:55:42 | 9.89E-05
138 | 3/11/2020 | 13:55:43 | 4.3329E-07
139 | 3/11/2020 | 13:55:44 | 3.9417E-07
140 | 3/11/2020 | 13:55:45 | 5.7924E-07
141 | 3/11/2020 | 13:55:46 | 0.00016973
142 | 3/11/2020 | 13:55:47 | 0.00018698
143 | 3/11/2020 | 13:55:48 | 0.00018766
144 | 3/11/2020 | 13:55:49 | 9.4597E-05
145 | 3/11/2020 | 13:55:50 | 4.9197E-07
146 | 3/11/2020 | 13:55:51 | 4.2577E-07
147 | 3/11/2020 | 13:55:52 | 1.154E-06
148 | 3/11/2020 | 13:55:53 | 0.00017099
149 | 3/11/2020 | 13:55:54 | 0.00018754
150 | 3/11/2020 | 13:55:55 | 0.00018916
151 | 3/11/2020 | 13:55:56 | 9.1692E-05
152 | 3/11/2020 | 13:55:57 | 4.8295E-07
153 | 3/11/2020 | 13:55:58 | 4.3029E-07
154 | 3/11/2020 | 13:55:59 | 2.1185E-06
155 | 3/11/2020 | 13:56:00 | 0.00017617
156 | 3/11/2020 | 13:56:01 | 0.00018838
157 | 3/11/2020 | 13:56:02 | 0.00018805
158 | 3/11/2020 | 13:56:03 | 8.7483E-05
159 | 3/11/2020 | 13:56:04 | 4.4383E-07
160 | 3/11/2020 | 13:56:05 | 4.7693E-07
161 | 3/11/2020 | 13:56:06 | 3.3989E-06
162 | 3/11/2020 | 13:56:07 | 0.00018088
163 | 3/11/2020 | 13:56:08 | 0.00018979
164 | 3/11/2020 | 13:56:09 | 0.0001891
165 | 3/11/2020 | 13:56:10 | 0.00018978
166 | 3/11/2020 | 13:56:11 | 3.1585E-05
167 | 3/11/2020 | 13:56:12 | 4.6038E-07
168 | 3/11/2020 | 13:56:13 | 4.9649E-07
169 | 3/11/2020 | 13:56:14 | 4.7647E-05
170 | 3/11/2020 | 13:56:15 | 0.00018893
171 | 3/11/2020 | 13:56:16 | 0.00018914
172 | 3/11/2020 | 13:56:17 | 0.00018849
173 | 3/11/2020 | 13:56:18 | 2.914E-05
174 | 3/11/2020 | 13:56:19 | 3.2195E-07
175 | 3/11/2020 | 13:56:20 | 3.2496E-07
176 | 3/11/2020 | 13:56:21 | 4.9546E-05
177 | 3/11/2020 | 13:56:22 | 0.00018914
178 | 3/11/2020 | 13:56:23 | 0.00018824
179 | 3/11/2020 | 13:56:24 | 0.00018856
180 | 3/11/2020 | 13:56:25 | 1.9759E-05
181 | 3/11/2020 | 13:56:26 | 4.2577E-07
182 | 3/11/2020 | 13:56:27 | 4.7843E-07
183 | 3/11/2020 | 13:56:28 | 6.0289E-05
184 | 3/11/2020 | 13:56:29 | 0.00018838
185 | 3/11/2020 | 13:56:30 | 0.00018837
186 | 3/11/2020 | 13:56:31 | 0.0001881
187 | 3/11/2020 | 13:56:32 | 1.7229E-05
188 | 3/11/2020 | 13:56:33 | 4.5135E-07
189 | 3/11/2020 | 13:56:34 | 4.7091E-07
190 | 3/11/2020 | 13:56:35 | 6.9842E-05
191 | 3/11/2020 | 13:56:36 | 0.00018759
192 | 3/11/2020 | 13:56:37 | 0.00018896
193 | 3/11/2020 | 13:56:38 | 0.00018347
194 | 3/11/2020 | 13:56:39 | 6.0455E-06
195 | 3/11/2020 | 13:56:40 | 4.3329E-07
196 | 3/11/2020 | 13:56:41 | 4.5435E-07
197 | 3/11/2020 | 13:56:42 | 7.9694E-05
198 | 3/11/2020 | 13:56:43 | 0.00018835
199 | 3/11/2020 | 13:56:44 | 0.00018864
200 | 3/11/2020 | 13:56:45 | 0.00017827
201 | 3/11/2020 | 13:56:46 | 2.4013E-06
202 | 3/11/2020 | 13:56:47 | 4.1975E-07
203 | 3/11/2020 | 13:56:48 | 3.8063E-07
204 | 3/11/2020 | 13:56:49 | 9.4429E-05
205 | 3/11/2020 | 13:56:50 | 0.00018885
206 | 3/11/2020 | 13:56:51 | 0.00018802
207 | 3/11/2020 | 13:56:52 | 0.00016753
208 | 3/11/2020 | 13:56:53 | 7.3873E-07
209 | 3/11/2020 | 13:56:54 | 4.664E-07
210 | 3/11/2020 | 13:56:55 | 4.2577E-07
211 | 3/11/2020 | 13:56:56 | 0.00010206
212 | 3/11/2020 | 13:56:57 | 0.00018793
213 | 3/11/2020 | 13:56:58 | 0.00018682
214 | 3/11/2020 | 13:56:59 | 0.00015841
215 | 3/11/2020 | 13:57:00 | 3.4452E-07
216 | 3/11/2020 | 13:57:01 | 2.8685E-07
217 | 3/11/2020 | 13:57:02 | 2.9788E-07
218 | 3/11/2020 | 13:57:03 | 2.392E-07
219 | 3/11/2020 | 13:57:04 | 0.00014783
220 | 3/11/2020 | 13:57:05 | 0.00018733
221 | 3/11/2020 | 13:57:06 | 0.00018709
222 | 3/11/2020 | 13:57:07 | 0.00011643
223 | 3/11/2020 | 13:57:08 | 4.5135E-07
224 | 3/11/2020 | 13:57:09 | 4.5587E-07
225 | 3/11/2020 | 13:57:10 | 4.3329E-07
226 | 3/11/2020 | 13:57:11 | 0.00015117
227 | 3/11/2020 | 13:57:12 | 0.00018826
228 | 3/11/2020 | 13:57:13 | 0.00018758
229 | 3/11/2020 | 13:57:14 | 0.00010945
230 | 3/11/2020 | 13:57:15 | 4.1825E-07
231 | 3/11/2020 | 13:57:16 | 4.2728E-07
232 | 3/11/2020 | 13:57:17 | 4.6489E-07
233 | 3/11/2020 | 13:57:18 | 0.0001573
234 | 3/11/2020 | 13:57:19 | 0.00018759
235 | 3/11/2020 | 13:57:20 | 0.00018848
236 | 3/11/2020 | 13:57:21 | 0.00010879
237 | 3/11/2020 | 13:57:22 | 4.6339E-07
238 | 3/11/2020 | 13:57:23 | 4.3931E-07
239 | 3/11/2020 | 13:57:24 | 4.4684E-07
240 | 3/11/2020 | 13:57:25 | 0.0001598
241 | 3/11/2020 | 13:57:26 | 0.00018919
242 | 3/11/2020 | 13:57:27 | 0.00018837
243 | 3/11/2020 | 13:57:28 | 0.00010667
244 | 3/11/2020 | 13:57:29 | 4.8144E-07
245 | 3/11/2020 | 13:57:30 | 4.7693E-07
246 | 3/11/2020 | 13:57:31 | 4.8445E-07
247 | 3/11/2020 | 13:57:32 | 0.00016271
248 | 3/11/2020 | 13:57:33 | 0.00018783
249 | 3/11/2020 | 13:57:34 | 0.00018794
250 | 3/11/2020 | 13:57:35 | 0.00010411
251 | 3/11/2020 | 13:57:36 | 4.5586E-07
252 | 3/11/2020 | 13:57:37 | 4.6639E-07
253 | 3/11/2020 | 13:57:38 | 4.6038E-07
254 | 3/11/2020 | 13:57:39 | 0.00016348
255 | 3/11/2020 | 13:57:40 | 0.00018845
256 | 3/11/2020 | 13:57:41 | 0.00018854
257 | 3/11/2020 | 13:57:42 | 0.00010065
258 | 3/11/2020 | 13:57:43 | 3.1744E-07
259 | 3/11/2020 | 13:57:44 | 3.4753E-07
260 | 3/11/2020 | 13:57:45 | 7.0413E-07
261 | 3/11/2020 | 13:57:46 | 0.0001688
262 | 3/11/2020 | 13:57:47 | 0.00018863
263 | 3/11/2020 | 13:57:48 | 0.00018919
264 | 3/11/2020 | 13:57:49 | 8.5478E-05
265 | 3/11/2020 | 13:57:50 | 4.4232E-07
266 | 3/11/2020 | 13:57:51 | 3.8214E-07
267 | 3/11/2020 | 13:57:52 | 4.4582E-06
268 | 3/11/2020 | 13:57:53 | 0.00018037
269 | 3/11/2020 | 13:57:54 | 0.00018747
270 | 3/11/2020 | 13:57:55 | 0.00018836
271 | 3/11/2020 | 13:57:56 | 7.8943E-05
272 | 3/11/2020 | 13:57:57 | 4.6489E-07
273 | 3/11/2020 | 13:57:58 | 4.4985E-07
274 | 3/11/2020 | 13:57:59 | 5.1303E-07
275 | 3/11/2020 | 13:58:00 | 5.525E-05
276 | 3/11/2020 | 13:58:01 | 0.00018826
277 | 3/11/2020 | 13:58:02 | 0.00018832
278 | 3/11/2020 | 13:58:03 | 0.0001879
279 | 3/11/2020 | 13:58:04 | 2.1509E-05
280 | 3/11/2020 | 13:58:05 | 4.1073E-07
281 | 3/11/2020 | 13:58:06 | 4.7091E-07
282 | 3/11/2020 | 13:58:07 | 6.161E-05
283 | 3/11/2020 | 13:58:08 | 0.00018786
284 | 3/11/2020 | 13:58:09 | 0.00018845
285 | 3/11/2020 | 13:58:10 | 0.00018777
286 | 3/11/2020 | 13:58:11 | 1.5777E-05
287 | 3/11/2020 | 13:58:12 | 4.5887E-07
288 | 3/11/2020 | 13:58:13 | 4.4533E-07
289 | 3/11/2020 | 13:58:14 | 6.3394E-05
290 | 3/11/2020 | 13:58:15 | 0.00018773
291 | 3/11/2020 | 13:58:16 | 0.00018748
292 | 3/11/2020 | 13:58:17 | 0.000187
293 | 3/11/2020 | 13:58:18 | 1.3373E-05
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

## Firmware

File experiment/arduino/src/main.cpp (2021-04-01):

#include <Arduino.h>
#include "experiment_config.h"
#include "LED.h"
#include "TLC5947_optoPlate.h"

#include <avr/wdt.h> // To reboot arduino

//define number of LED drivers and assign microcontroller

#define NUM_TLC5947 12
#define DATA_PIN 4
#define CLK_PIN 5
#define LATCH_PIN 6
#define OUTPUT_EN 7

#define START_CODE 225
#define RESET_CODE 226

Adafruit_TLC5947 tlc = Adafruit_TLC5947(NUM_TLC5947, CLK_PIN, DATA_PIN, LATCH_PIN); //creates LED driver object


// True every second
bool newSecond = false;

bool needLedSetup = false;

#define BUFF_SIZE 64
uint8_t TF_buff[BUFF_SIZE];
uint8_t numBytes;

// To restart the OptoPlate through serial
void reboot() {
  wdt_disable();
  wdt_enable(WDTO_15MS);
  while (1) {}
}


// Wrights the intensities to a buffer in tlc, to flash the values to the LEDs tlc.wright must be called 
void setLED(uint8_t led, uint16_t well, uint16_t intensity)
{
  if (led == 0)
  {
    tlc.setPWM((uint16_t)((int)(well / 12) + 8 * (well % 12)), intensity);
  }
  else if (led == 1)
  {
    tlc.setPWM((uint16_t)(well + 192), intensity);
  }
  else if (led == 2)
  {
    tlc.setPWM((uint16_t)((int)(well / 12) + 8 * (well % 12) + 96), intensity);
  }
}

void init1HzTimer()
{
  //Set up 1hz interrupt timer
  cli(); //stop interrupts
  //set timer1 interrupt at 1Hz
  TCCR1A = 0; // set entire TCCR1A register to 0
  TCCR1B = 0; // same for TCCR1B
  TCNT1 = 0;  //initialize counter value to 0
  // set compare match register for 1hz increments
  OCR1A = 15624; // = (16*10^6) / (1*1024) - 1 (must be <65536)
  // turn on CTC mode
  TCCR1B |= (1 << WGM12);
  // Set CS10 and CS12 bits for 1024 prescaler
  TCCR1B |= (1 << CS12) | (1 << CS10);
  // enable timer compare interrupt
  TIMSK1 |= (1 << OCIE1A);
  sei();
}

ISR(TIMER1_COMPA_vect)
{
  newSecond = true;
}

void setup()
{
  // Set up LED state machine
  LED_init();
  
  Serial.begin(115200);
  // If connected to a PC wait for a caracter before continuing
  delay(100);
  #ifdef WAIT_FOR_SERIAL
    while (Serial.read() != START_CODE) {
      delay(100);
    }
  #endif
  
  tlc.begin();
  // Turn off all LEDs
  for (uint16_t i = 0; i < NUMB_WELLS; i++)
  {
#if NUMB_WELL_LEDS < 3
    setLED(0, i, 0);
    setLED(1, i, 0);
#endif
#if NUMB_WELL_LEDS == 3
    setLED(0, i, 0);
    setLED(1, i, 0);
    setLED(2, i, 0);
#endif
  }
 tlc.write();
 if (OUTPUT_EN >= 0)
  {
    pinMode(OUTPUT_EN, OUTPUT);
    digitalWrite(OUTPUT_EN, HIGH);
  }
  
  init1HzTimer();
}

void loop()
{

  if (newSecond)
  {
    // Set new values on LEDs
    tlc.write();
    needLedSetup = true;
    newSecond = false;
  }
  else if (needLedSetup)
  {
    // Run the state machine for all the LED and prepare the new intensities to be flashed in the new second
    needLedSetup = false;

    for (uint8_t i = 0; i < NUMB_WELLS; i++)
    {

#if NUMB_WELL_LEDS == 1
      // When only 1 color of LED is used the two LED in a well share the same LED state machine
      uint8_t intensity = LED_updateGetIntensity(0, i);
      setLED(0, i, calibrateIntensity(0, i, intensity));
      setLED(1, i, calibrateIntensity(1, i, intensity));

#endif
#if NUMB_WELL_LEDS == 2
      // When multiple colors of LED are used they get their own state machine
      uint8_t intensity = LED_updateGetIntensity(0, i);
      setLED(0, i, calibrateIntensity(0, i, intensity));
      intensity = LED_updateGetIntensity(1, i);
      setLED(1, i, calibrateIntensity(1, i, intensity));
#endif
#if NUMB_WELL_LEDS == 3
      uint8_t intensity = LED_updateGetIntensity(0, i);
      setLED(0, i, calibrateIntensity(0, i, intensity));
      intensity = LED_updateGetIntensity(1, i);
      setLED(1, i, calibrateIntensity(1, i, intensity));
      intensity = LED_updateGetIntensity(2, i);
      setLED(2, i, calibrateIntensity(2, i, intensity));
#endif
    }
  }

  // Read Serial and update the TinyFrame listener
  numBytes = Serial.available();
  if(numBytes > 0) {
    for (uint8_t n = 0; n < numBytes; n++) {
     uint8_t byte = Serial.read();
     uint8_t well= byte & 0x7F;
     if( byte == RESET_CODE) {
       reboot();
     } else if( (byte & 0x80) > 0) {
       LED_wellEnable(well);
     } else
     {
       LED_wellDisable(well);
      #if NUMB_WELL_LEDS == 1 || NUMB_WELL_LEDS == 2
        setLED(0, well, 0);
        setLED(1, well, 0);
      #endif
      #if NUMB_WELL_LEDS == 3
        setLED(0, well, 0);
        setLED(1, well, 0);
        setLED(2, well, 0);
      #endif
     }
    }
    tlc.write();
  }
  
}

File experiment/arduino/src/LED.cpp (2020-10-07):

#include "LED.h"

pulseState pulseStates[NUMB_WELL_LEDS][NUMB_WELLS];   // The current state of the LED
uint16_t pulseCounts[NUMB_WELL_LEDS][NUMB_WELLS];     // Number of pulses that have been looped through
uint16_t pulseTimeCounts[NUMB_WELL_LEDS][NUMB_WELLS]; // Time in seconds since start of high phase of pulse or low phase of pulse
bool enabled[NUMB_WELL_LEDS][NUMB_WELLS]; //  Enable/disable LED 


// Reads the EEPROM and returns the calibration value
uint8_t getCalibrationValue(uint8_t led, uint8_t well)
{
#if NUMB_WELL_LEDS < 3
    return EEPROM.read(well * 2 + led);
#else
    return EEPROM.read(well * 3 + led);
#endif
}

void LED_init()
{
    for (uint8_t well = 0; well < NUMB_WELLS; well++)
    {
        for (uint8_t led = 0; led < NUMB_WELL_LEDS; led++)
        {
            // Initiate state machine
            pulseStates[led][well] = P_START;
            pulseCounts[led][well] = 0;
            pulseTimeCounts[led][well] = 0;
            enabled[led][well] = true;
        }
    }
}

uint8_t LED_updateGetIntensity(const uint8_t led, const uint8_t well)
{

    bool ledHigh = false;
    pulseTimeCounts[led][well]++;
    switch (pulseStates[led][well])
    {
    case P_START:
        if (pulseTimeCounts[led][well] >= pgm_read_word_near(&(pusleStartTimes[led][well])))
        {   
            pulseStates[led][well] = P_HIGH_SP_HIGH;
            pulseTimeCounts[led][well] = 0;

            ledHigh = true;
        }
        break;

    case P_HIGH_SP_HIGH:
        if (pulseTimeCounts[led][well] >= pgm_read_word_near(&(pulseHighTimes[led][well])))
        {
            pulseStates[led][well] = P_LOW;
            pulseTimeCounts[led][well] = 0;
        }
        else
        {
            uint16_t spHighTime = pgm_read_word_near(&(subpulseHighTimes[led][well]));
            uint16_t spLowTime = pgm_read_word_near(&(subpulseLowTimes[led][well]));
            if (pulseTimeCounts[led][well] % (spHighTime + spLowTime) == spHighTime)
            {
                pulseStates[led][well] = P_HIGH_SP_LOW;
            }
            else
            {
                ledHigh = true;
            }
        }
        break;
    case P_HIGH_SP_LOW:
        if (pulseTimeCounts[led][well] >= pgm_read_word_near(&(pulseHighTimes[led][well])))
        {
            pulseStates[led][well] = P_LOW;
            pulseTimeCounts[led][well] = 0;
        }
        else
        {
            uint16_t spHighTime = pgm_read_word_near(&(subpulseHighTimes[led][well]));
            uint16_t spLowTime = pgm_read_word_near(&(subpulseLowTimes[led][well]));
            if (pulseTimeCounts[led][well] % (spHighTime + spLowTime) == 0)
            {
                pulseStates[led][well] = P_HIGH_SP_HIGH;
                ledHigh = true;
            }
        }
        break;

    case P_LOW:
        if (pulseTimeCounts[led][well] >= pgm_read_word_near(&(pulseLowTimes[led][well])))
        {
            pulseCounts[led][well]++;
            pulseTimeCounts[led][well] = 0;
            if (pulseCounts[led][well] >= pgm_read_word_near(&(pulseNumbs[led][well])))
            {
                pulseStates[led][well] = DONE;
            }
            else
            {
                pulseStates[led][well] = P_HIGH_SP_HIGH;
                ledHigh = true;
            }
        }
        break;

    case DONE:
        break;
    }

    if (ledHigh && enabled[led][well])
    {
        return (uint8_t)pgm_read_byte_near(&amplitudes[led][well]);
    }
    else
    {
        return 0;
    }
}

void LED_disable(const uint8_t led, const uint8_t well) {
    enabled[led][well] = false;
}

void LED_enable(const uint8_t led, const uint8_t well) {
    enabled[led][well] = true;
}

void LED_wellDisable(const uint8_t well) {
    for(int i = 0; i < NUMB_WELL_LEDS; i++) {
        LED_disable(i, well);
    }
}

void LED_wellEnable(const uint8_t well) {
    for(int i = 0; i < NUMB_WELL_LEDS; i++) {
        LED_enable(i, well);
    }
}

uint16_t calibrateIntensity(const uint8_t led, const uint8_t well, const uint8_t intensity)
{
    return ((uint16_t)intensity * getCalibrationValue(led, well)) / 16;
}

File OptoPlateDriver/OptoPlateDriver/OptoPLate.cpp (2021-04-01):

#include "OptoPlate.h"


HANDLE hComm; 

void sendSerial(HANDLE  & hComm, char data[255], int dLength);
void readSerial(HANDLE  & hComm, char data[255], int & dLength);
void closeSerial(HANDLE & hComm);
void initSerial(HANDLE & hComm, const char * ComPortName);

int OptoPlateConnect(int portNumber) {
	std::string portName = std::string("COM") + std::to_string(portNumber);
	initSerial(hComm, portName.c_str());
	return 1;
}

int OptoPlateConnectAuto() {

	std::string portName;

	TCHAR lpTargetPath[5000]; // buffer to store the path of the COMPORTS
	DWORD test;
	bool gotPort = 0; // in case the port is not found

	for (int i = 0; i < 50; i++) // checking ports from COM0 to COM255
	{
		std::string str = std::to_string(i);
		std::string ComName = std::string("COM") + str; // converting to COM0, COM1, COM2

		test = QueryDosDevice(ComName.c_str(), (LPSTR)lpTargetPath, 5000);

		// Test the return value and error if any
		if (test != 0) //QueryDosDevice returns zero if it didn't find an object
		{
			portName = ComName;
			gotPort = 1; // found port
		}
	}
	if (gotPort) {
		initSerial(hComm, portName.c_str());
	}
	else {
		printf("Error: unable to find COMport.");
	}
	return 1;
}


int OptoPlateDisconnect() {
    closeSerial(hComm);
	return 1;
}

int OptoPlateSignalStart() {
	char buff = 225;
	sendSerial(hComm, &buff, 1);
	return 1;
}

int OptoPlateReset() {
	char buff = 226;
	sendSerial(hComm, &buff, 1);
	return 1;
}



int OptoPlateDisableLED(int LEDindex) {
	char buff = (char)LEDindex;
	sendSerial(hComm, &buff, 1);
	return 1;
}

int OptoPlateEnableLED(int LEDindex) {
	char buff = 1<<7 | (char)LEDindex;
	sendSerial(hComm, &buff, 1);
	return 1;
}

int getInvIndex(int LEDindex) {
	int col = (LEDindex) / 12;
	int row = (LEDindex) % 12;
	int invLEDindex = (col + 1) * 12 - row-1;
	return invLEDindex;
}

int OptoPlateDisableLEDinv(int LEDindex) {
	OptoPlateDisableLED(getInvIndex(LEDindex));
	return 1;
}
int OptoPlateEnableLEDinv(int LEDindex) {
	OptoPlateEnableLED(getInvIndex(LEDindex));
	return 1;
}


void sendSerial(HANDLE  & hComm, char data[255], int dLength) {
    BOOL  Status;                          // Status of the various operations 
    DWORD dNoOFBytestoWrite = dLength;     // No of bytes to write into the port
    DWORD dNoOfBytesWritten = 0;     // No of bytes written to the port

    Status = WriteFile(hComm,        // Handle to the Serial port
                      data,     // Data to be written to the port
                      dNoOFBytestoWrite,  //No of bytes to write
                      &dNoOfBytesWritten, //Bytes written
                      NULL);

}

void readSerial(HANDLE  & hComm, char data[255], int & dLength) {
  
  DWORD dwEventMask;                     // Event mask to trigger
  BOOL  Status;                          // Status of the various operations 
  char  TempChar;                        // Temperory Character
  DWORD NoBytesRead;                     // Bytes read by ReadFile()
  int i = 0;
	
  Status = WaitCommEvent(hComm, &dwEventMask, NULL); //Wait for the character to be received
  if (Status == FALSE)
    {
      printf("\n    Error! in Setting WaitCommEvent()");
      dLength = 0;
    }
  else //If  WaitCommEvent()==True Read the RXed data using ReadFile();
    {
      do
        {
          Status = ReadFile(hComm, &TempChar, sizeof(TempChar), &NoBytesRead, NULL);
          data[i] = TempChar;
          i++;
        } 
      while (NoBytesRead > 0);  
      dLength = i;
    }	
}

void closeSerial(HANDLE & hComm) {
  CloseHandle(hComm);//Closing the Serial Port
}


void initSerial(HANDLE & hComm, const char * ComPortName) {
			BOOL  Status;                          // Status of the various operations 
		
			std::string ComPortNameModified = "\\\\.\\" + std::string(ComPortName);
			hComm = CreateFile(ComPortNameModified.c_str(),                  // Name of the Port to be Opened
		                        GENERIC_READ | GENERIC_WRITE, // Read/Write Access
								0,                            // No Sharing, ports cant be shared
								NULL,                         // No Security
							    OPEN_EXISTING,                // Open existing port only
		                        0,                            // Non Overlapped I/O
		                        NULL);                        // Null for Comm Devices

			if (hComm == INVALID_HANDLE_VALUE)
				printf("\n    Error! - Port %s can't be opened\n", ComPortName);
			else
				printf("\n    Port %s Opened\n ", ComPortName);
			
			DCB dcbSerialParams = { 0 };                         // Initializing DCB structure
			dcbSerialParams.DCBlength = sizeof(dcbSerialParams);

			Status = GetCommState(hComm, &dcbSerialParams);      //retreives  the current settings

			if (Status == FALSE)
				printf("\n    Error! in GetCommState()");

			dcbSerialParams.BaudRate = CBR_115200;      // Setting BaudRate = 115200
			dcbSerialParams.ByteSize = 8;             // Setting ByteSize = 8
			dcbSerialParams.StopBits = ONESTOPBIT;    // Setting StopBits = 1
			dcbSerialParams.Parity = NOPARITY;        // Setting Parity = None 

			Status = SetCommState(hComm, &dcbSerialParams);  //Configuring the port according to settings in DCB 

			if (Status == FALSE)
				{
					printf("\n    Error! in Setting DCB Structure");
				}
			else //If Successfull display the contents of the DCB Structure
				{
					printf("\n\n    Setting DCB Structure Successfull\n");
					printf("\n       Baudrate = %d", dcbSerialParams.BaudRate);
					printf("\n       ByteSize = %d", dcbSerialParams.ByteSize);
					printf("\n       StopBits = %d", dcbSerialParams.StopBits);
					printf("\n       Parity   = %d", dcbSerialParams.Parity);
				}

			COMMTIMEOUTS timeouts = { 0 };
			timeouts.ReadIntervalTimeout         = 500;
			timeouts.ReadTotalTimeoutConstant    = 50;
			timeouts.ReadTotalTimeoutMultiplier  = 10;
			timeouts.WriteTotalTimeoutConstant   = 50;
			timeouts.WriteTotalTimeoutMultiplier = 10;
			
			if (SetCommTimeouts(hComm, &timeouts) == FALSE)
				printf("\n\n    Error! in Setting Time Outs");
			else
				printf("\n\n    Setting Serial Port Timeouts Successfull");

			
			Status = SetCommMask(hComm, EV_RXCHAR); //Configure Windows to Monitor the serial device for Character Reception
	
			if (Status == FALSE)
				printf("\n\n    Error! in Setting CommMask");
			else
				printf("\n\n    Setting CommMask successfull");

}

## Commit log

2019-10-24 Namechange to fit Arduino convetion
2019-10-28 Variable namechange and added feature where 0 duration indicates LED permanently off
2019-11-07 Working prototype
2019-11-21 LEDs can now blink in square wave pattern in differen phases
2019-12-05 Changed initializing of LEDs
2019-12-05 Fixed bug where program crashes from to many leds and added dual calibration
2020-02-18 Added files from calibration
    [ROUND01_LED01_WELLS01.csv, ROUND01_LED01_WELLS02.csv, ROUND01_LED02_WELLS01.csv, ROUND01_LED02_WELLS02.csv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]
2020-03-02 Cal round 0 added
    [ROUND01_LED01_WELLS01.csv, ROUND01_LED01_WELLS02.csv, ROUND01_LED02_WELLS01.csv, ROUND01_LED02_WELLS02.csv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]
2020-03-05 Calibrated optoPlate02
    [HOLD.csv, ROUND01_LED01_WELLS01.csv, ROUND01_LED01_WELLS02.csv, ROUND01_LED02_WELLS01.csv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]
2020-03-05 Measure without
    Calibration script will now just measure or plot input/output relationships
    [RAMP_WELLS01.csv, ROUND04_LED01_WELLS02.csv, ROUND04_LED02_WELLS01.csv, ROUND04_LED02_WELLS02.csv]
2020-03-05 Measured variance at fixed intensity
    [CALIBRATED_WELLS01.csv, CALIBRATED_WELLS02.csv, UNCALIBRATED_WELLS01.csv, UNCALIBRATED_WELLS02.csv]
2020-03-05 Plotted calibration
2020-03-10 Updated calibration
2020-03-11 Calibrated optoPlate 2
    [CALIBRATED_WELLS01.csv, CALIBRATED_WELLS02.csv, HOLD.csv, RAMP_WELLS01.csv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]
2020-03-11 Calibrated optoPla\te02
    [CALIBRATED_WELLS01.csv, CALIBRATED_WELLS02.csv, RAMP_WELLS01.csv, RAMP_WELLS02.csv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]
2020-04-20 Updated to new led intensity pattern
2020-05-07 Added Calibration experiments
2020-05-12 Added example LED configuration
2020-05-12 Added mechanical parts
    [Aluminum Plate.SLDDRW, Aluminum Plate.SLDPRT, AssemblyMicroscopeAdapter.SLDASM, Base Plate.SLDDRW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]
2020-05-12 Renamed calibration round 0
2020-05-12 Moved Checkers back to calibration
2020-05-12 Renamed calibration script
2020-05-12 Recoved lost data
    [CALIBRATED_WELLS01.csv, CALIBRATED_WELLS02.csv, RAMP_WELLS01.csv, RAMP_WELLS02.csv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]
2020-05-27 Shortened filenames to fit better in article
    [AssemblyMicroscopeAdaptor.SLDASM, MicroscopeAdaptorLowerPart.SLDPRT, MicroscopeAdaptorUpperPart.SLDPRT, OptoPlateToNunc265300.SLDPRT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]
2020-05-28 Changed case sensitive names
2020-06-19 Added independent LED set calibration
2020-06-22 Removed subpulseCount - working 2 LED
2020-06-22 Updated independent calibration script
2020-06-24 Moved independent LED set calibration to main script
2020-07-24 Unable LEDs will continue to update it's state
2020-09-03 Added configuration for moungting 96 well plate upside down
    [OptoPlateAdapterToNunc265300_96.SLDPRT, OptoPlateAdapterToNunc265300_96_Assembly.SLDASM, OptoPlateAdapterToNunc265300_96_BottomHalf.sldprt, OptoPlateAdapterToN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]
2020-09-03 Added STL files
    [OptoPlateAdapterToNunc265300_96_BottomHalf.sldprt, OptoPlateAdapterToNunc265300_96_BottomHalf_Default.STL, OptoPlateAdapterToNunc265300_96_Top_Default.STL, Opt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]
2020-10-02 Create experiment from xlsx
    [optoPlate_config_test.xlsx]
2020-12-30 Pass xlsx folder path to createExperiment() for easy output
    [optoPlate_config_test.xlsx]
2021-01-20 Added wait_for_signal features
    [optoPlate_config_test.xlsx]
2021-01-22 added get_led_patterns
    gets led patterns from experiment and saves to table for easy plotting
2021-04-01 Updated adaptor filenames, added new ones
    [OptoPlateAdapterToNunc265300_96_InversionInsert.SLDPRT, OptoPlateAdapterToNunc265300_96_InversionInsert_Default.STL, OptoPlateAdapterToNunc265300_96_Tophalf_In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]
2021-04-22 Documentation and TECAN adaptor
    Updated script instructions, added example plate map, updated STL for TECAN adaptor, placed older scripts into own folder
    [Aluminum Plate.SLDDRW, Aluminum Plate.SLDPRT, Base Plate.SLDDRW, Base Plate.SLDPRT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]
2022-07-05 Added supp calibration protocol
2022-08-22 Added quick calibration script
    [ROUND01_LED01.csv, ROUND01_LED02.csv]
2022-11-30 Added JOB file for quick calibration protocol
    [ROUND01_LED01.csv, ROUND01_LED02.csv]
2024-01-21 Added example_plate_map
    Added example_plate_map as a useful resource for how to layout an experiment along with the optoPlate configuration.
    [example_plate_map.xlsx]
2024-03-08 Update README.md
    Added where to find assembly instructions (in mechanical)
